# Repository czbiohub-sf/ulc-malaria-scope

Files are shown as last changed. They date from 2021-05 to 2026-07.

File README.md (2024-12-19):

# Remoscope: a label-free imaging cytometer for malaria diagnostics

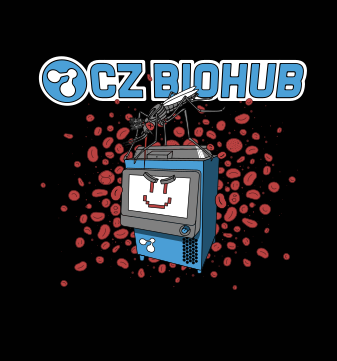
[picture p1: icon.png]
An artistic rendition of the Remoscope


## Introduction
This repository hosts instrument control software for the Remoscope, an automated and low-cost malaria diagnostic system, requiring minimal user training. The Remoscope was developed by the Bioengineering team at the Chan Zuckerberg Biohub San Francisco (CZBSF). The Remoscope images unstained fresh whole blood in liquid form and can screen up to two million red blood cells for _Plasmodium falciparum_ parasites. 

Please see our preprint here:



The Remoscope runs off a Raspberry Pi 4 Model B 8GB and an Intel Neural Compute Stick 2 (no longer available) to accelerate on-device neural network inferencing. The instrument control software is written in Python 3.7.3.

## Repository structure

```
├── ulc_mm_package
│   ├── utilities
│   ├── summary_report
│   ├── neural_nets
│   ├── image_processing
│   ├── hardware
│   ├── configs
│   ├── QtGUI
│   ├── scope_constants.py
├── OS_instructions
│   ├── OS_setup.md
│   └── OS_flash.md
├── architecture_description
├── setup.py
└── README.md
```

For a more detailed description of each folder and its scripts, see the `architecture_description/` folder.

## Installation and use

NOTE: If you are using a version downstream of commit `283a823` on `develop` (2024-03-06), you will need to install the `stats_utils` module. To do so, in the root directory run
```
python3 -m pip install -e .
```

### Option 1: Clone the image

1. Flash a pre-existing image to an SD card (must be at least 32GB), see `OS_flash.md`

### Option 2: Manual install

1. Follow the instructions under `OS_instructions`.

## Operation

To start the software, navigate to ulc_mm_package/QtGUI and run `python3 oracle.py`.

To use developer mode, navigate to ulc_mm_package/QtGUI and run `python3 dev_run.py`. This opens a GUI with manual hardware control for debugging purposes.

#### Related repositories
1. Object detection - YOGO: https://github.com/czbiohub-sf/yogo
2. Autofocus - SSAF: https://github.com/czbiohub-sf/ulc-malaria-autofocus
3. Data processing utilities / model evaluations: https://github.com/czbiohub-sf/lfm-data-utilities/
4. Statistics utilities: https://github.com/czbiohub-sf/remo-stats-utils

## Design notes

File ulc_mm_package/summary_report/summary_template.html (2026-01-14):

# Remoscope experiment report: {{ dataset_name }}

# RESEARCH USE ONLY - NOT FOR CLINICAL USE

/

Estimated parasitemia is indicated by central bar below, with 95% confidence interval outlined by box. 

{# Experiment metadata #}

Experiment metadata
Operator ID | {{ operator_id }}
Non-identifying sample ID | {{ sample_id }}
Notes | {{ notes }}
Flowcell ID | {{ flowcell_id }}

{# Estimated sample composition #}
Estimated sample composition
Class | Raw count | Parasitemia (p/uL) | Parasitemia (%)

{% for key, vals in class_name_to_cell_count.items() %}
{{key}} | {{vals[0]}} | {{vals[1]}} | {{vals[2]}}

{% endfor %} Parasitemia includes asexual stages only. {# Thumbnails #}

### Parasite thumbnails

{% for key in all_thumbnails %}
{{key.upper()}}

{% for row in all_thumbnails[key]|batch(10, "") %}

{% for filename in row %} {% if filename | length > 0 %} 
{{".".join(filename.split("_")[-1].split(".")[:2])[:4]}}
{% endif %} {% endfor %}

{% endfor %} {% endfor %} {# OPTIONAL PLOTS FOR INTERNAL USE #} {% if DEBUG_SUMMARY_REPORT %} {# Metadata plots #}

### Per-Image Metadata Plot

 {# YOGO Performance Plots #}

#### Cell counts over time



#### Confidence histograms



#### Objectness histograms

 {% endif %}

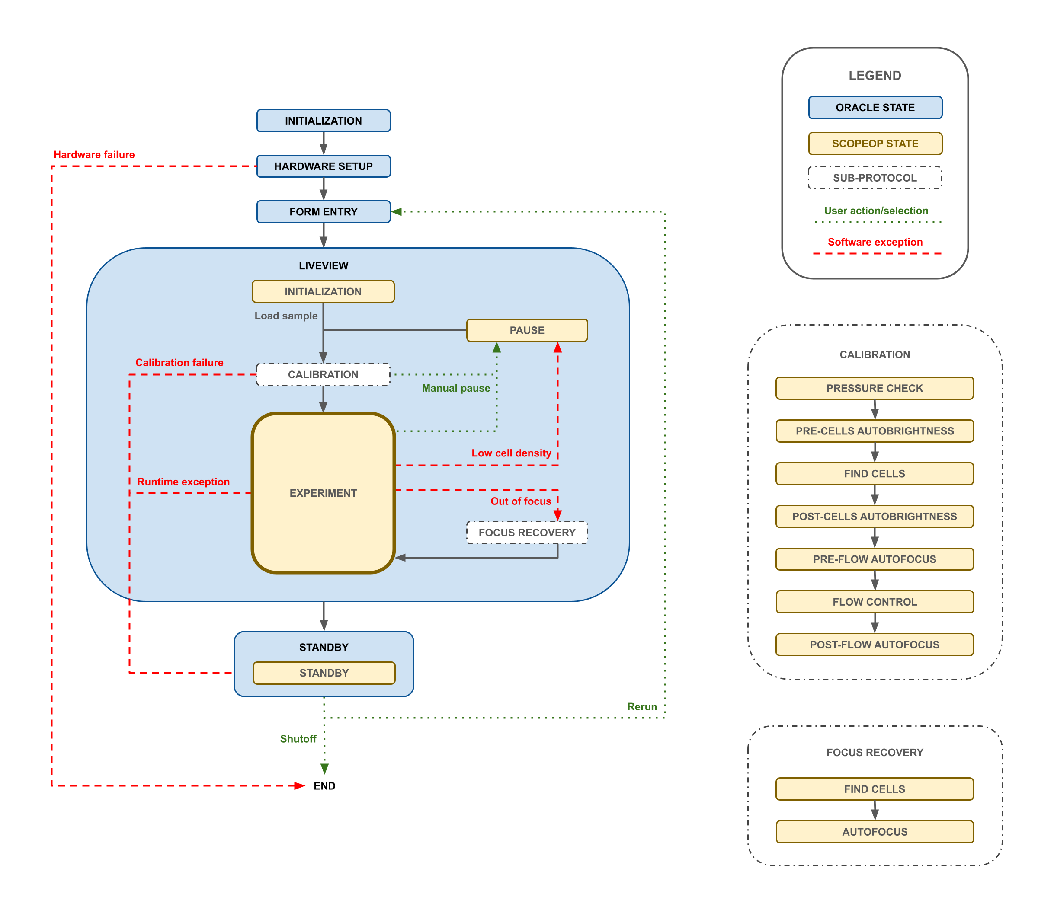
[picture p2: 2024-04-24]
software flowchart.png

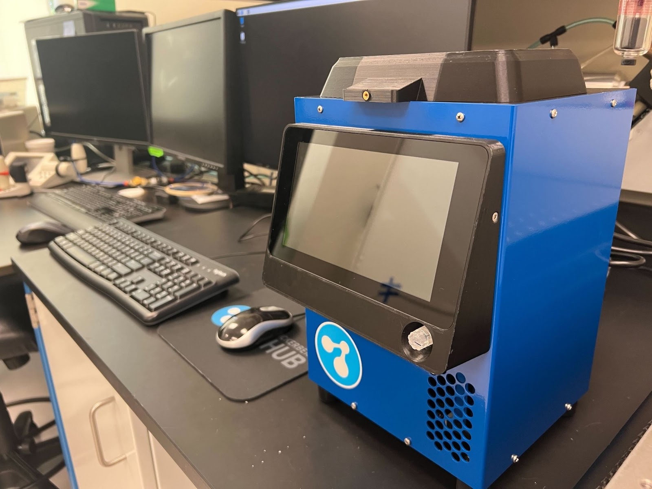
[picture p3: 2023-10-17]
pic_of_scope.jpg

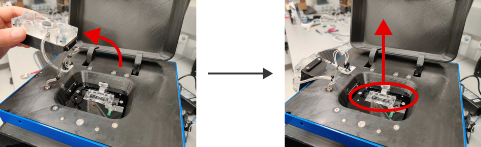
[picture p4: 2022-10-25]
ulc_mm_package/QtGUI/gui_images/remove_infographic.png

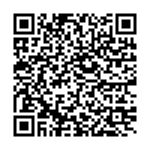
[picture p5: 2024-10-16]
ulc_mm_package/QtGUI/gui_images/QR/no-cells.png

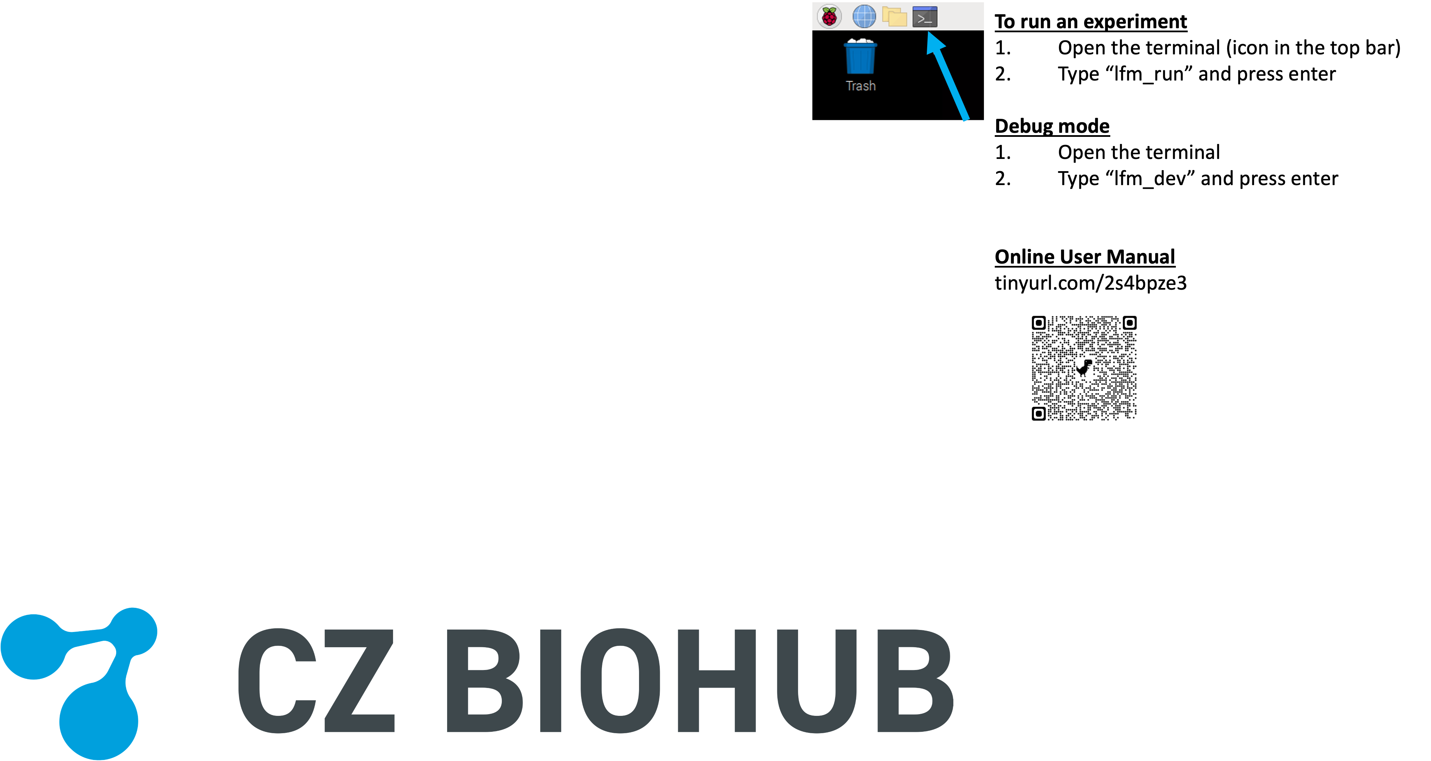
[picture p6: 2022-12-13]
ulc_mm_package/utilities/rpi_bg.png

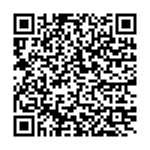
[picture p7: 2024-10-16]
ulc_mm_package/QtGUI/gui_images/QR/flowrate.png

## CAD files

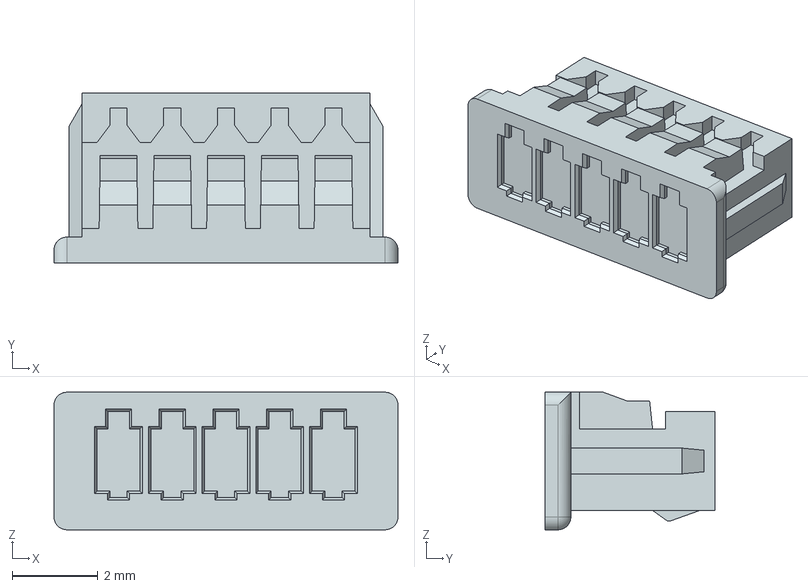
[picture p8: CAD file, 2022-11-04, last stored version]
pcb/ulc-mm/3d models/Molex_PicoBlade_533980571_Conn.step
8.00 x 3.95 x 3.20 mm

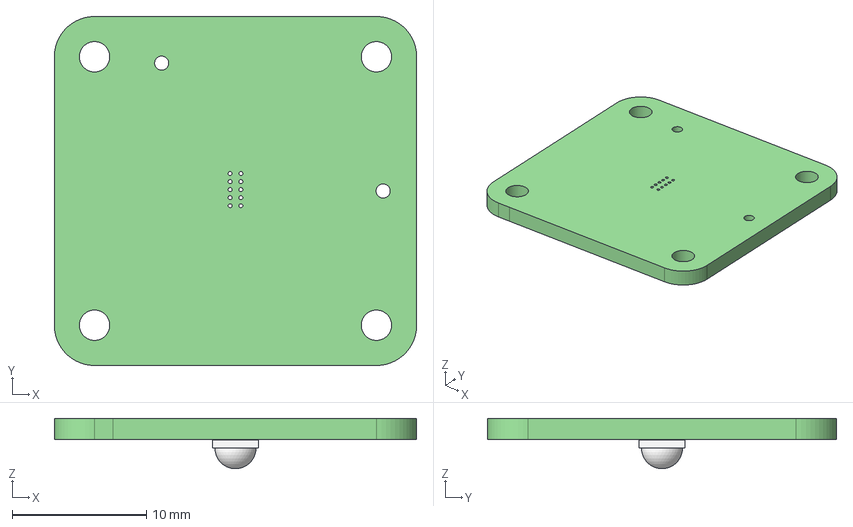
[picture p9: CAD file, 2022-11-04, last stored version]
pcb/ulc-mm/ulc-mm-led.step
27.0 x 26.0 x 3.76 mm

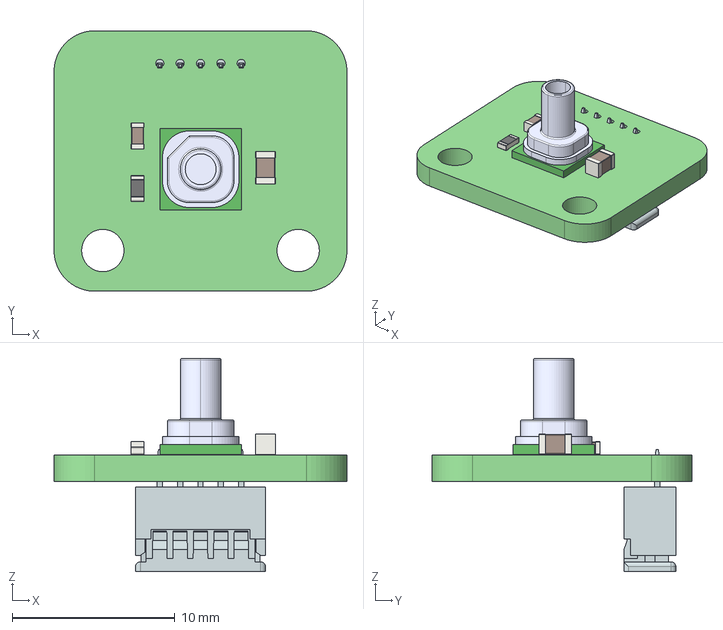
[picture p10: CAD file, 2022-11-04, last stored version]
pcb/ulc-mm/mprls.step
18.0 x 16.0 x 13.1 mm

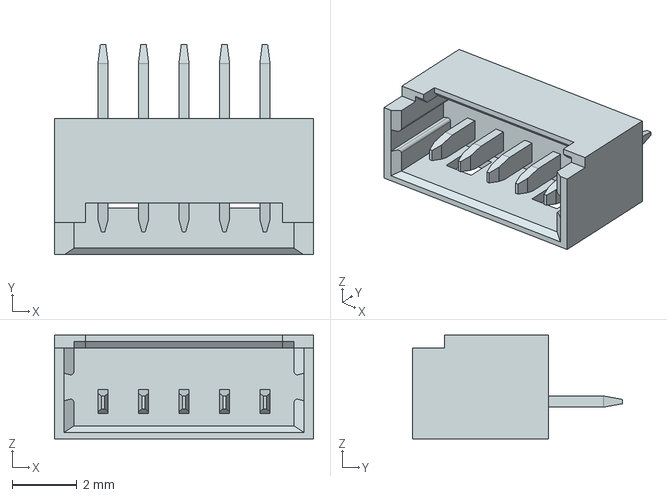
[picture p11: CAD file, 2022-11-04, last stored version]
pcb/ulc-mm/3d models/Molex_530470510.stp
8.00 x 6.50 x 3.20 mm

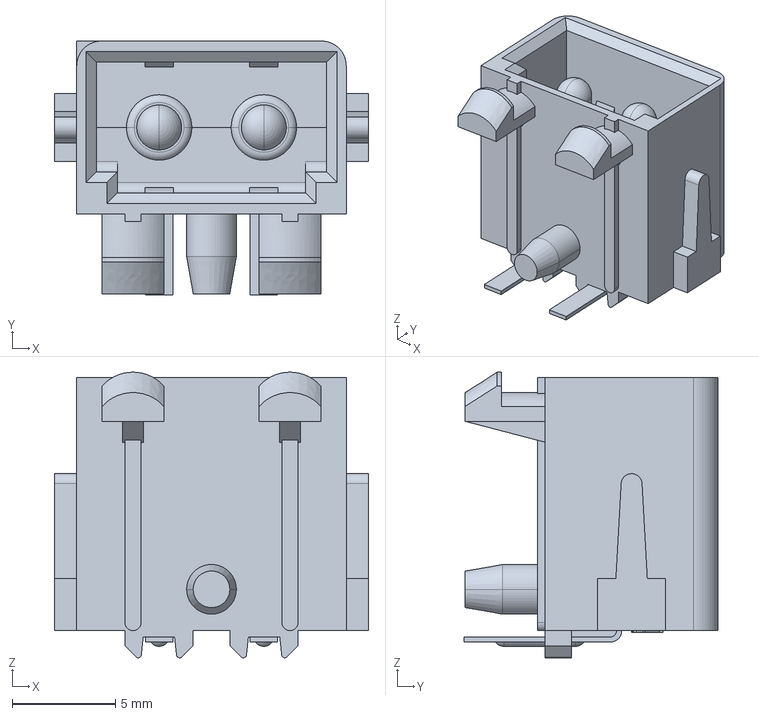
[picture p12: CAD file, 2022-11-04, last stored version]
pcb/ulc-mm/3d models/TE_794120-1-g-3d.stp
15.2 x 12.3 x 13.9 mm

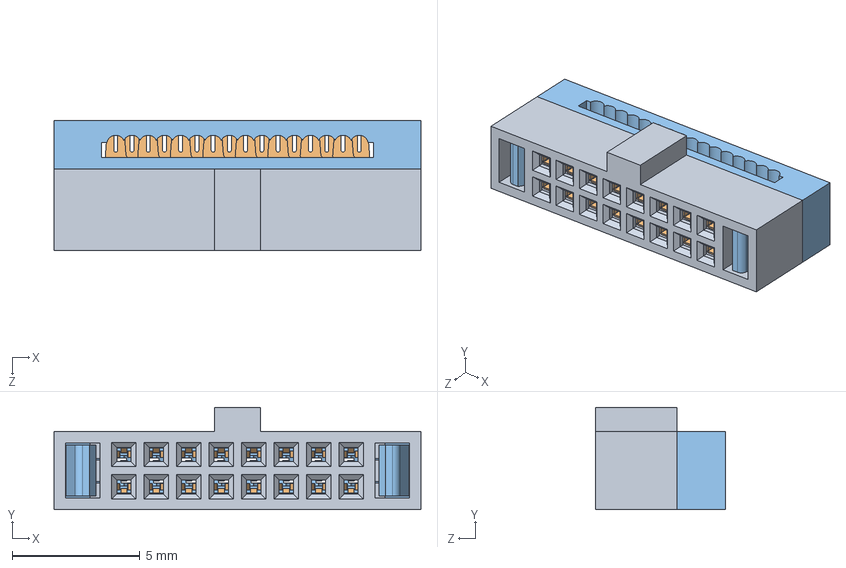
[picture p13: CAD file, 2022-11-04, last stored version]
pcb/ulc-mm/3d models/3230-16-0102-00 3D.STEP
14.4 x 4.00 x 5.10 mm
802-4412-440XX x 16
801-4412-16-ZIF

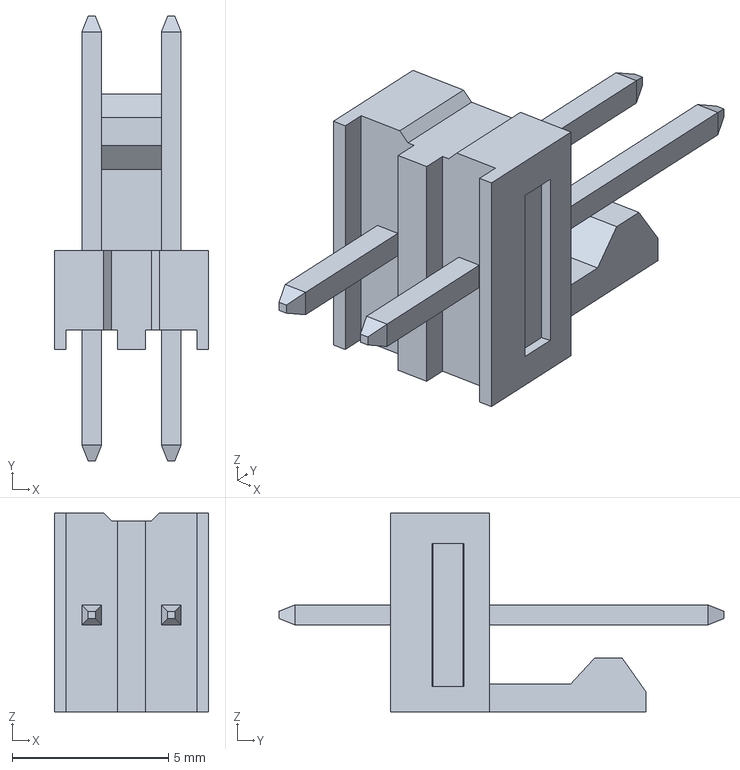
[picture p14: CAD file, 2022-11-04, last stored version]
pcb/ulc-mm/3d models/Molex_KK_022232021.stp
4.93 x 14.2 x 6.35 mm

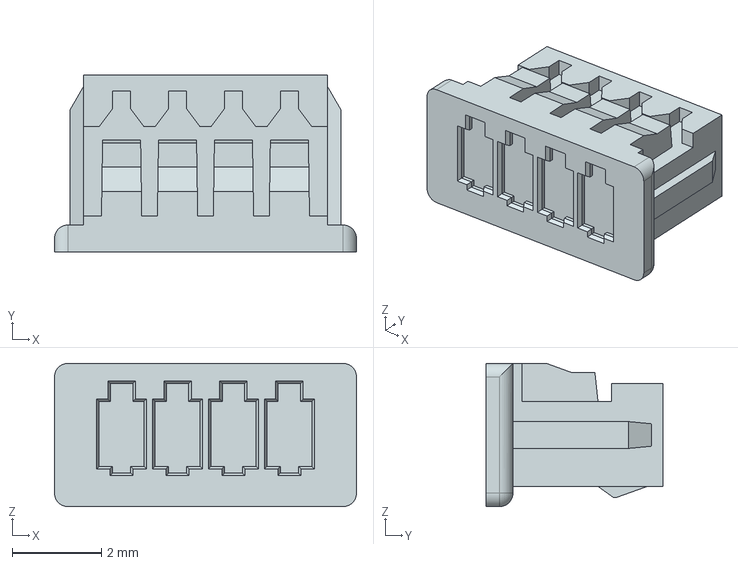
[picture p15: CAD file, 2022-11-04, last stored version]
pcb/ulc-mm/3d models/Molex_PicoBlade_530470410_Conn.step
6.75 x 3.95 x 3.20 mm

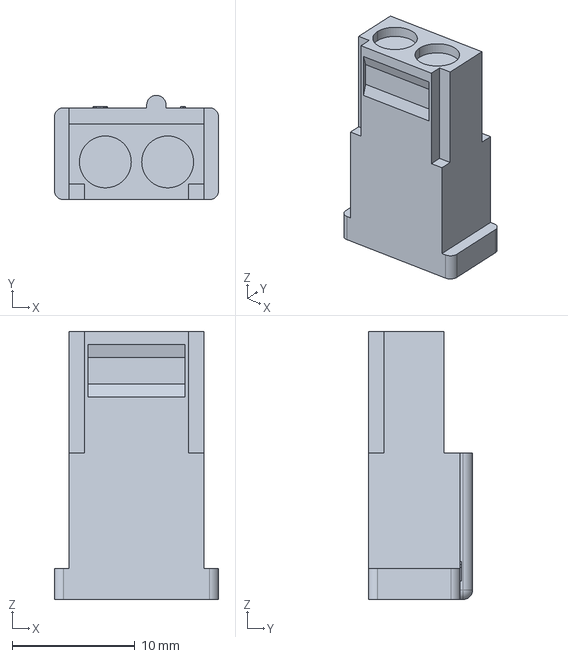
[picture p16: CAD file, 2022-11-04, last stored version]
pcb/ulc-mm/3d models/c-1-480318-0-r-3d.stp
13.4 x 8.51 x 21.8 mm

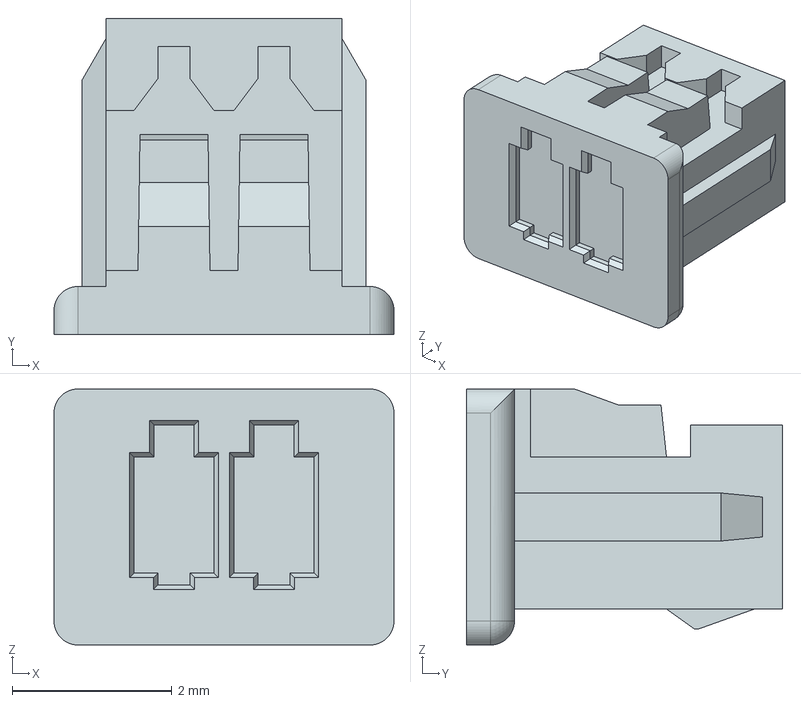
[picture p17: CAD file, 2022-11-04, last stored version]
pcb/ulc-mm/3d models/Molex_PicoBlade_530470210_Conn.step
4.25 x 3.95 x 3.20 mm

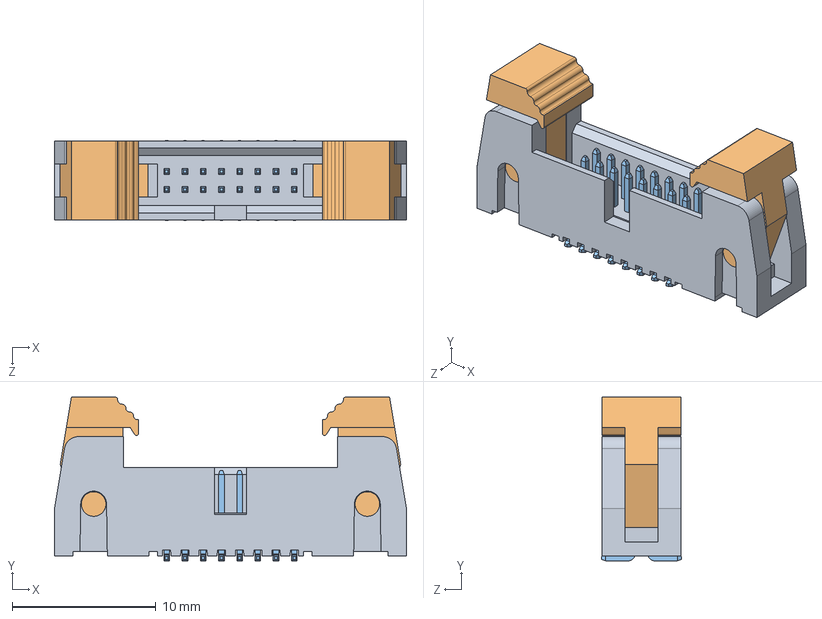
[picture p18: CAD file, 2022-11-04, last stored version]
pcb/ulc-mm/3d models/3210-16-003-12-00 3D.STEP
24.5 x 11.4 x 5.60 mm
804A-2196-01 x 2
802-2196SM x 16

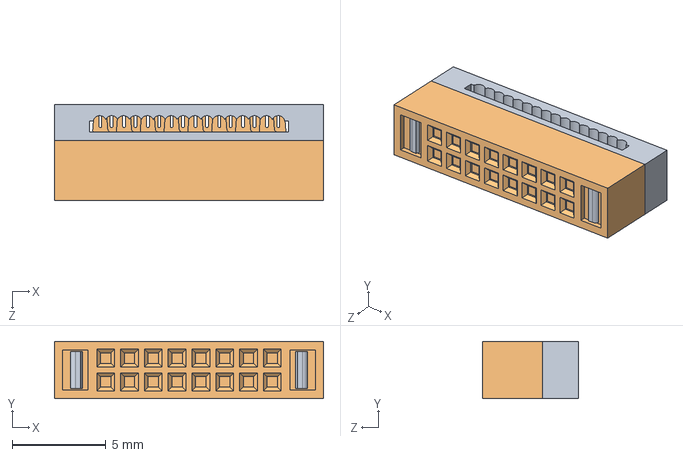
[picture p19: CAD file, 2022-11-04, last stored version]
pcb/ulc-mm/3d models/3230-16-0101-00 3D.STEP
14.4 x 3.05 x 5.10 mm

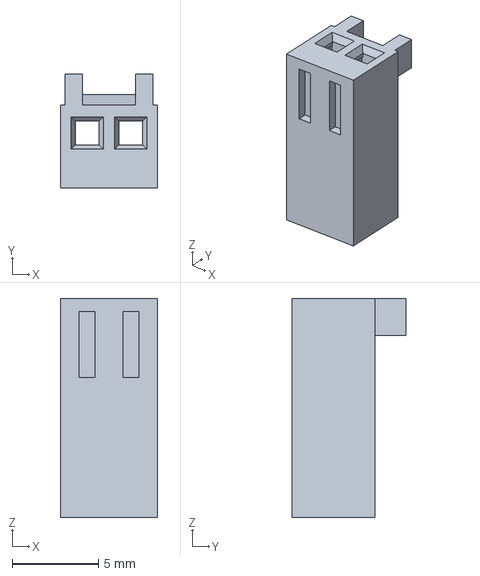
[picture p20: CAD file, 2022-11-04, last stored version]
pcb/ulc-mm/3d models/022013027.stp
5.64 x 6.63 x 12.7 mm

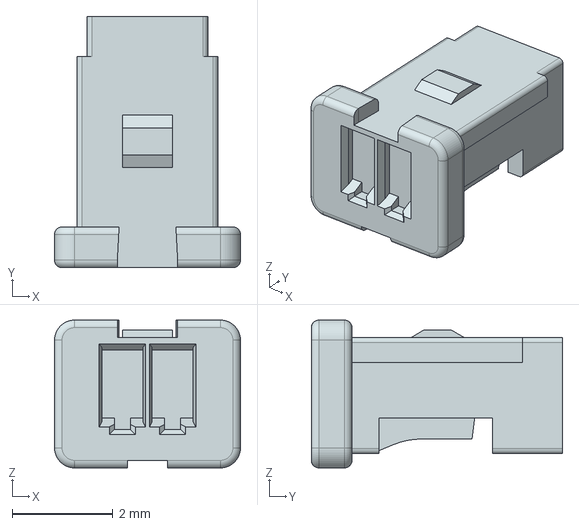
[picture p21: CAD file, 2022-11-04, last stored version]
pcb/ulc-mm/3d models/5013300200.stp
3.70 x 5.00 x 2.94 mm

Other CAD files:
pcb/ulc-mm/3d models/5013310207.stp

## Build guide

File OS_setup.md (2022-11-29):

Install Raspbian GNU/Linux 11 (bullseye) on a fresh 64GB SD card. Make sure to update the OS
hostname and wifi/password by pressing shift-ctrl-x. After it is flashed, pop it into a Pi and
follow the commands below.

### Starting out
```console
sudp apt update
sudo apt upgrade
```

### Install ulc-malaria-scope
```console
mkdir Documents && cd Documents
git clone https://github.com/czbiohub/ulc-malaria-scope.git
cd ulc-malaria-scope
pip3 install -e .
```

### Install cmake and some req'd libraries
```console
sudo apt install -y cmake
sudo apt install libusb-1.0-0-dev
sudo apt install libatlas-base-dev
```

### Install Openvino

Please note: I found that a *lot* of the documentation for the installation of Openvino is simply wrong. I suspect that it is way out of date, and nobody at Intel bother to update it. The instructions I have below are the result of what I found to work, but it could change in future Openvino versions. A *large* part of figuring it out was looking at the post-install setup scripts that openvino wrote (primarily setupvars.sh and install_NCS_udev_rules.sh), figuring out what those scripts were *supposed* to do, and doing those steps. At the very least, you learn a lot about linux when installing all of this ;)

```console
git clone https://github.com/openvinotoolkit/openvino.git
git checkout tags/2022.1.1
git submodule update --init --recursive
mkdir build && cd build

# Takes a long time! Maybe ~4 hrs?
cmake \
  -DCMAKE_BUILD_TYPE=Release \
  -DENABLE_PYTHON=ON \
  -DPYTHON_EXECUTABLE="/usr/bin/python3"  \
  -DPYTHON_LIBRARY="/usr/lib/arm-linux-gnueabihf/libpython3.9.so"  \
  -DPYTHON_INCLUDE_DIR="/usr/include/python3.9"  \
  -DCYTHON_EXECUTABLE="/home/pi/.local/bin/cython"  \
  -DENABLE_OV_TF_FRONTEND_ENABLE=OFF  \
  -DENABLE_OV_PDPD_FRONTEND_ENABLE=OFF  \
  -DENABLE_SAMPLES=OFF  \
  -DENABLE_HETERO=OFF  \
  .. && make --jobs=$(nproc --all)
```

### Add the openvino Python libraries to the `PYTHONPATH`
```console
export PYTHONPATH=/home/pi/openvino/bin/armv7l/Release/lib/python_api/python3.9:$PYTHONPATH
```

### Manually update NCS2 udev rules

```console
# add yourself to group
sudo usermod -a -G users "$(whoami)"

# Now find the file "97-myriad-usbboot.rules" - for me, it was at
#   /home/pi/openvino/src/plugins/intel_myriad/third_party/mvnc/src/97-myriad-usbboot.rules
# If yours is in a different place, replace my path with yours below

sudo cp /home/pi/openvino/src/plugins/intel_myriad/third_party/mvnc/src/97-myriad-usbboot.rules /etc/udev/rules.d/
sudo udevadm control --reload-rules
sudo udevadm trigger
sudo ldconfig
```

### Install Vimba

I could not find Vimba for `armv71` online. I `rsync`'d the source (Vimba for Linux ARMv7 32-bit - Release Notes) from a previous Malaria Scope's OS and installed
from there.

I `rsync`'d it to `/opt/`, then
```console
cd /opt/Vimba_5_0/VimbaUSBTL
sudo ./Install.sh
sudo reboot
```

after reboot,

```console
cd /opt/Vimba_5_0/VimbaPython
sudo ./Install.sh
```

### Updating boot/config.txt
Now is a good time to take a breath. You've made it through the worst of it!
Add the following to `/boot/config.txt` (at the bottom, under `[all]` if it is there)

```console
start_x=1
dtoverlay=pwm-2chan,pin=12,func=4,pin2=13,func2=4
gpu_mem=128
```

Uncomment the following

```console
dtparam=i2c_arm=on
```

and now reboot.

### Install Others

To automate running the daemon at boot time, run:

```console
sudo systemctl enable pigpiod
```

### Instantiate our ulc-malaria-scope services

```console
sudo cp ~/Documents/ulc-malaria-scope/ulc_mm_package/utilities/systemd_init_scripts/init_led_pneumatic.service /lib/systemd/system
sudo chmod 644 /lib/systemd/system/init_led_pneumatic.service

sudo cp ~/Documents/ulc-malaria-scope/ulc_mm_package/utilities/systemd_init_scripts/fan.service /lib/systemd/system
sudo chmod 644 /lib/systemd/system/fan.service

sudo cp ~/Documents/ulc-malaria-scope/ulc_mm_package/utilities/systemd_init_scripts/ngrok.service /lib/systemd/system
sudo chmod 644 /lib/systemd/system/ngrok.service

sudo systemctl daemon-reload
sudo systemctl enable init_led_pneumatic.service
sudo systemctl enable fan.service
sudo systemctl enable ngrok.service
```

### Setting up ngrok
[Ngrok](https://ngrok.com/) is a service used to create `ssh` tunnels for accessing our scopes when they are behind private networks. At the time of writing (2022-11-28),
`ngrok` free-tier accounts allow you to have one persistent `ssh` connection per account.

Each scope needs to sign up for its own ngrok account (using a unique email) to be able to open and maintain a persistent ssh connection when the program starts.
To create an `ngrok` account, "Google Distribution email accounts" (i.e a forwarding received emails-only email account)
are sufficient. (According to IT at the time of writing, having an inbound/outbox default @czbiohub.org mailbox costs $7/mo.)

1. Ask IT to make a new account for the scope (and ask them to set your email as the forwarding one), e.g `lfm_newscope@czbiohub.org`
2. Sign up for `ngrok`, and note down the unique token.
3. Add this token to the scope's persistent environment variables by doing the following:
  - Open the bashrc file: `nano /home/pi/.bashrc`
  - Add `export NGROK_AUTH_TOKEN=<TOKEN_HERE>` to the bottom of the file.
4. TODO - set up the emailing functionality (`lfm_central@czbiohub.org`) (instead of each scope having a regular mailbox, which costs $7/mo for a
@czbiohub.org address, we have a single @czbiohub.org address that all the scopes use to send emails.) **Fill this in with details once we have this implemented.

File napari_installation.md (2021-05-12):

``` 
python3 -m venv napari
source napari/bin/activate
git clone https://github.com/czbiohub/napari-bb-annotations.git
git checkout pranathi-tflite
pip3 install --upgrade pip
pip3 install -r requirements_pip4.txt
sudo apt-get update
sudo apt-get install -y qt5-default pyqt5-dev pyqt5-dev-tools
```

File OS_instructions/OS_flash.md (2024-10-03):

# Flashing Instructions

99% of the time, you will be flashing one of these images. They are pre-made and ready specifically for the ULC Malaria Scope.

First, go get the Raspberry Pi Imager, if you don't have it already:

https://www.raspberrypi.com/software/

Second, go to the drive link:

https://drive.google.com/drive/u/0/folders/1lGbjsn2M_-sXlK0GY4xKjBfApmT6D6bf

Download the most recent image (currently in folder `2022-11-28 Base OS`) - it should be a `.img` or `.img.xz` file.

Now you simply flash the image. Open the program, plug in your SD card, and follow these options:

- For "Operating System", choose the `.img` or `.img.xz` file that you downloaded. This will be under "Custom" images
- For "Storage", choose the SD card

Next, press "shift-control-x" and update some settings such as the hostname and wifi.

Now, simply click "Write" and let the program finish.

## Post Flash

The first step here will be to insert the SD card into a Raspberry Pi and access it. Either `ssh` into it (make sure you have the hostname!), or plug a keyboard and monitor into it. Then, open a terminal, and run the following commands:

```console
cd ~/Documents/ulc-malaria-scope
git pull  # enter your ghp keys here, if necessary
```

### Setting up ngrok

[Ngrok](https://ngrok.com/) is a service used to create `ssh` tunnels for accessing our scopes when they are behind private networks. At the time of writing (2022-11-28), `ngrok` free-tier accounts allow you to have one persistent `ssh` connection per account.

Each scope needs to sign up for its own ngrok account (using a unique email) to be able to open and maintain a persistent ssh connection when the program starts. To create an `ngrok` account, "Google Distribution email accounts" (i.e a forwarding received emails-only email account) are sufficient. (According to IT at the time of writing, having an inbound/outbox default @czbiohub.org mailbox costs $7/mo.)

1. Ask IT to make a new account for the scope (and ask them to set your email as the forwarding one), e.g `lfm_newscope@czbiohub.org`
2. Sign up for `ngrok`, and note down the unique token.
3. Add this token to the scope's persistent environment variables by doing the following:
  - Open the bashrc file: `nano /home/pi/.bashrc`
  - Add `export NGROK_AUTH_TOKEN=<TOKEN_HERE>` to the bottom of the file.

### Setting up email functionality for sending back the ngrok address automatically
We use a non Biohub free gmail account to do basic email sending. The email, `lfmscope@gmail.com` sends an email to itself which is then forwarded to all the people on its forwarding list.
Gmail allows you to generate a unique password for each new device that you want to run on. Instructions to generate application-specific-passwords are [here](https://support.google.com/accounts/answer/185833?hl=en). Every microscope needs to have its own unique application-specific-password.
1. Create an application specific password using the `lfmscope@gmail.com` account
2. Place the password in the microscope's persistent environment variables (similar to what we did above for `ngrok`):
  - Open the bashrc file: `nano /home/pi/.bashrc`
  - Add `export GMAIL_TOKEN=<TOKEN_HERE>` to the bottom of the file.
3. Run both `oracle.py` and `dev_run.py` to ensure you're receiving emails and that there are no errors (for example, if you forget to set the email token, that will raise a custom `EmailError: no token set` error. Similarly if an ngrok token isn't set, a custom `NgrokError: no token set` error will be raised.)

### Setting up bash aliases
1. To avoid users having to enter in an arduous path into the terminal to run a program (which is also likely to be error-prone), we have a few bash aliases instead. These aliases are stored under `ulc-malaria-scope/ulc_mm_package/utilities/.bash_aliases`. `cd` into that directory and `cp` that file to `/home/pi`, i.e:
```
cd Documents/ulc-malaria-scope/ulc_mm_package/utilities
cp .bash_aliases /home/pi
```

The commands in the file can now be run from the terminal. At the time of writing (2022-12-09), the following commands are available:
- `lfm_run` - runs `oracle.py`
- `lfm_dev` - runs `dev_run.py`
- `send_address` - runs `email_utils.py` (attempts to send the ngrok address to `lfmscope@gmail.com`)

### Setting a default location
- In `~/.bashrc` add the following environment variable at the bottom of the file: `DEFAULT_SITE='NAME_OF_SITE'`. Note: the specified site MUST already be listed in `ulc_mm_package/QtGUI/gui_constants.py`'s `SITE_LIST` constant.

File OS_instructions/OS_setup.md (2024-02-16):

# Creating a fresh OS from scratch

These are instructions for creating a fresh OS image from scratch. 99% of the time, you will most likely just want to flash one of our pre-made images - see `OS_flash.md`.

## Full Installation Instructions

Install Raspbian GNU/Linux 11 (Bullseye) on a fresh 64GB SD card. Make sure to update the OS
hostname and wifi/password by pressing shift-ctrl-x. After it is flashed, pop it into a Pi and
follow the commands below.

```console
sudo apt update
sudo apt upgrade
```

## Optional but very nice things (axel would deeply appreciate it)

```console
sudo apt install tmux
cat << EOF > ~/.vimrc
set ai
set ruler
set hlsearch
set showmatch
set incsearch
set expandtab
set lazyredraw
set noswapfile
set splitbelow
set splitright
set ignorecase
set smartcase
set wildmenu
set number relativenumber

set mouse=a
set laststatus=2

set tabstop=2
set scrolloff=2
set shiftwidth=2
set softtabstop=2
set encoding=utf-8
set backspace=indent,eol,start

set signcolumn=yes:1
set fillchars+=vert:\|

set updatetime=250
set timeoutlen=300 ttimeoutlen=0

filetype plugin indent on
map <C-J> <C-W><C-J>
map <C-K> <C-W><C-K>
map <C-L> <C-W><C-L>
map <C-H> <C-W><C-H>
highlight clear SignColumn
EOF
```

### Install numba first, separately
Note: this section may become obsolete once we transition to a 64-bit OS. For now, these are the steps to get numba working on Raspbian 32-bit.

```
sudo apt install llvm-11
export LLVM_CONFIG=llvm-config-11 pip install llvmlite==0.37.0 --no-cache
pip install numba==0.56.0
```

### Install ulc-malaria-scope
```console
mkdir Documents && cd Documents
git clone https://github.com/czbiohub/ulc-malaria-scope.git
cd ulc-malaria-scope
pip3 install -e .
```

### Install cmake and some required libraries
```console
sudo apt install -y cmake
sudo apt install libusb-1.0-0-dev
sudo apt install libatlas-base-dev
pip3 install Cython>=0.29.33
```

### Install Openvino

Please note: I found that a *lot* of the documentation for the installation of Openvino is simply wrong. I suspect that it is way out of date, and nobody at Intel bother to update it. The instructions I have below are the result of what I found to work, but it could change in future Openvino versions. A *large* part of figuring it out was looking at the post-install setup scripts that openvino wrote (primarily setupvars.sh and install_NCS_udev_rules.sh), figuring out what those scripts were *supposed* to do, and doing those steps. At the very least, you learn a lot about linux when installing all of this ;)

```console
cd ~
git clone https://github.com/openvinotoolkit/openvino.git
cd openvino
git checkout tags/2022.1.1
git submodule update --init --recursive
mkdir build && cd build

# Takes a long time! Maybe ~4 hrs?
cmake \
  -DCMAKE_BUILD_TYPE=Release \
  -DENABLE_PYTHON=ON \
  -DPYTHON_EXECUTABLE="/usr/bin/python3"  \
  -DPYTHON_LIBRARY="/usr/lib/arm-linux-gnueabihf/libpython3.9.so"  \
  -DPYTHON_INCLUDE_DIR="/usr/include/python3.9"  \
  -DCYTHON_EXECUTABLE="/home/pi/.local/bin/cython"  \
  -DENABLE_OV_TF_FRONTEND_ENABLE=OFF  \
  -DENABLE_OV_PDPD_FRONTEND_ENABLE=OFF  \
  -DENABLE_SAMPLES=OFF  \
  -DENABLE_HETERO=OFF  \
  .. && make --jobs=$(nproc --all)
```

If you are running a 64 bit OS, swap out `-DPYTHON_LIBRARY="/usr/lib/arm-linux-gnueabihf/libpython3.9.so"` with `-DPYTHON_LIBRARY="/usr/lib/aarch64-linux-gnu/libpython3.9.so"`.

### Add the openvino Python libraries to the `PYTHONPATH`

for a 32 bit OS,
```console
echo "export PYTHONPATH=/home/pi/openvino/bin/armv7l/Release/lib/python_api/python3.9:$PYTHONPATH" >> ~/.bashrc
```

and if you are running a 64 bit OS,
```console
echo "export PYTHONPATH=/home/pi/openvino/bin/aarch64/Release/lib/python_api/python3.9:$PYTHONPATH" >> ~/.bashrc
```

### Manually update NCS2 udev rules

```console
# add yourself to group
sudo usermod -a -G users "$(whoami)"

# Now find the file "97-myriad-usbboot.rules" - for me, it was at
#   /home/pi/openvino/src/plugins/intel_myriad/third_party/mvnc/src/97-myriad-usbboot.rules
# If yours is in a different place, replace my path with yours below

sudo cp /home/pi/openvino/src/plugins/intel_myriad/third_party/mvnc/src/97-myriad-usbboot.rules /etc/udev/rules.d/
sudo udevadm control --reload-rules
sudo udevadm trigger
sudo ldconfig
```

### Install Vimba

Download and uncompress Vimba for your version of the software:

- [Vimba 64 bit](https://drive.google.com/file/d/1_0ckwfBUPX-drv2zrvJkzIj39QkT-eUr/view?usp=share_link)
- [Vimba 32 bit](https://drive.google.com/file/d/16OUi32I5QPsywLyl9qaezAkova_Dz53e/view?usp=sharing)

`rsync` it to `/opt/`, then

```console
cd /opt/Vimba_5_0/VimbaUSBTL
sudo ./Install.sh
sudo reboot
```

after reboot,

```console
cd /opt/Vimba_5_0/VimbaPython
sudo ./Install.sh
```

### Updating boot/config.txt
Now is a good time to take a breath. You've made it through the worst of it!
Add the following to `/boot/config.txt` (at the bottom, under `[all]` if it is there)

```console
start_x=1
dtoverlay=pwm-2chan,pin=12,func=4,pin2=13,func2=4
gpu_mem=128
```

Uncomment the following

```console
dtparam=i2c_arm=on
```

### Install Others

To automate running the daemon at boot time, run:

```console
sudo systemctl enable pigpiod
```

### Instantiate our ulc-malaria-scope services

```console
sudo cp ~/Documents/ulc-malaria-scope/ulc_mm_package/utilities/systemd_init_scripts/init_led_pneumatic.service /lib/systemd/system
sudo chmod 644 /lib/systemd/system/init_led_pneumatic.service

sudo cp ~/Documents/ulc-malaria-scope/ulc_mm_package/utilities/systemd_init_scripts/fan.service /lib/systemd/system
sudo chmod 644 /lib/systemd/system/fan.service

sudo systemctl daemon-reload
sudo systemctl enable init_led_pneumatic.service
sudo systemctl enable fan.service
```

and now reboot.

### Setting up the SSD
Instructions on Confluence here: https://czbiohub.atlassian.net/l/cp/SW5bEMJ4

Tldr:
**If choosing to format as exFAT**
1. This process is straightforward - connect the SSD to your Mac, run DiskUtility, right-click and select format, choose exFAT.
2. Rename the drive to SamsungSSD by right-clicking on it and renaming.

**For ext4, the process is a little more involved**
**Warning - formatting as ext4 means it'll be a pain to try to read the SSD on your Mac computer. The performance gains (if any) are dubious, so this section should be ignored. Likely better to just use exFAT and skip all the headache**
I outline the procedure here for MacOS, but the high-level steps are similar for Windows (it may just involve different tools)

1. Connect the SSD and use e2fsprogs to format:

  - `brew install e2fsprogs`

  - `diskutil list` (note down the name of the 4TB SSD, e.g /dev/disk2)

  - Run `sudo $(brew --prefix e2fsprogs)/sbin/mkfs.ext4 /dev/disk2`

2. Connect the SSD to a Pi / Linux system

  - Set the name of the SSD

  - Run `lsblk` and note the location of the SSD (e.g `sda` or `sda2`)

  - Run `e2label /dev/sda SamsungSSD`

3. Set the permissions of the SSD

  - `cd /media/pi/` (or wherever the SSD is located)

  - `sudo chmod 777 SamsungSSD/`

### Congrats!

You are done.

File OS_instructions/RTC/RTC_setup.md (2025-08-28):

# RTC

The RTC ensures the Pi has accurate datetime regardless of Internet connection and power loss. To stay up to date, the RTC also needs to be updated whenever the Pi has correct time via network time protocol (NTP) syncing.

The instructions below configure the OS for the following behavior:
- If Pi is disconnected from internet at startup: Update system time from RTC
- If Pi successfully syncs to NTP via internet: Update RTC from system (NTP) time

## Setup instructions

The following files need to live in the Pi's `/etc/` directory:
- `rc.local` sets behavior on boot
- `dhcpcd.exit-hook` sets behavior on Internet connection

Ensure both files have executable permission:
```
sudo chmod +x rc.local
sudo chmod +x dhcpcd.exit-hook
```

## Tests (optional)

Reboot after adding the above files to start the RTC before testing.

### RTC in use

Verify system vs RTC time using `timedatectl` in terminal. You will see a printout like this:
```
               Local time: Mon 2025-08-25 15:42:07 PDT
           Universal time: Mon 2025-08-25 22:42:07 UTC
                 RTC time: Mon 2025-08-25 22:42:08
                Time zone: America/Los_Angeles (PDT, -0700)
System clock synchronized: yes
              NTP service: active
          RTC in local TZ: no
```

If the RTC did not successfully start, RTC time will be listed as `n/a`.

### System updated by RTC

Test the use case where there's no Internet connection:

First, turn off NTP sync, otherwise the time will automatically be corrected when `timedatectl` is run.
```
timedatectl set-ntp false
```

Then, manually write an incorrect date/time to the RTC.
```
sudo hwclock --set --date "01/01/2001 00:00:00"
```

Run `timedatectl` to verify the RTC's datetime.

Turn wifi off and reboot. The system time should now be the incorrect RTC time. Be patient as it can take up to 1 min for the system time to update after reconnection.

_NOTE: If you ever want to overwrite system time using the RTC on the spot, run `sudo hwclock -s`._

### RTC updated bt system (NTP) time

Test the use case where the Pi reconnects to Internet:

Turn on wifi when it was previously off or reboot Pi. Both the system time and RTC time should be correct and can be verified by running `timedatectl`

_NOTE: If you ever want to overwrite the RTC using the NTP time on the spot, run `sudo hwclock -w`._

## Supplementary info
- [hwclock](https://linux.die.net/man/8/hwclock) tool
- [timedatectl](https://www.freedesktop.org/software/systemd/man/latest/timedatectl.html) tool

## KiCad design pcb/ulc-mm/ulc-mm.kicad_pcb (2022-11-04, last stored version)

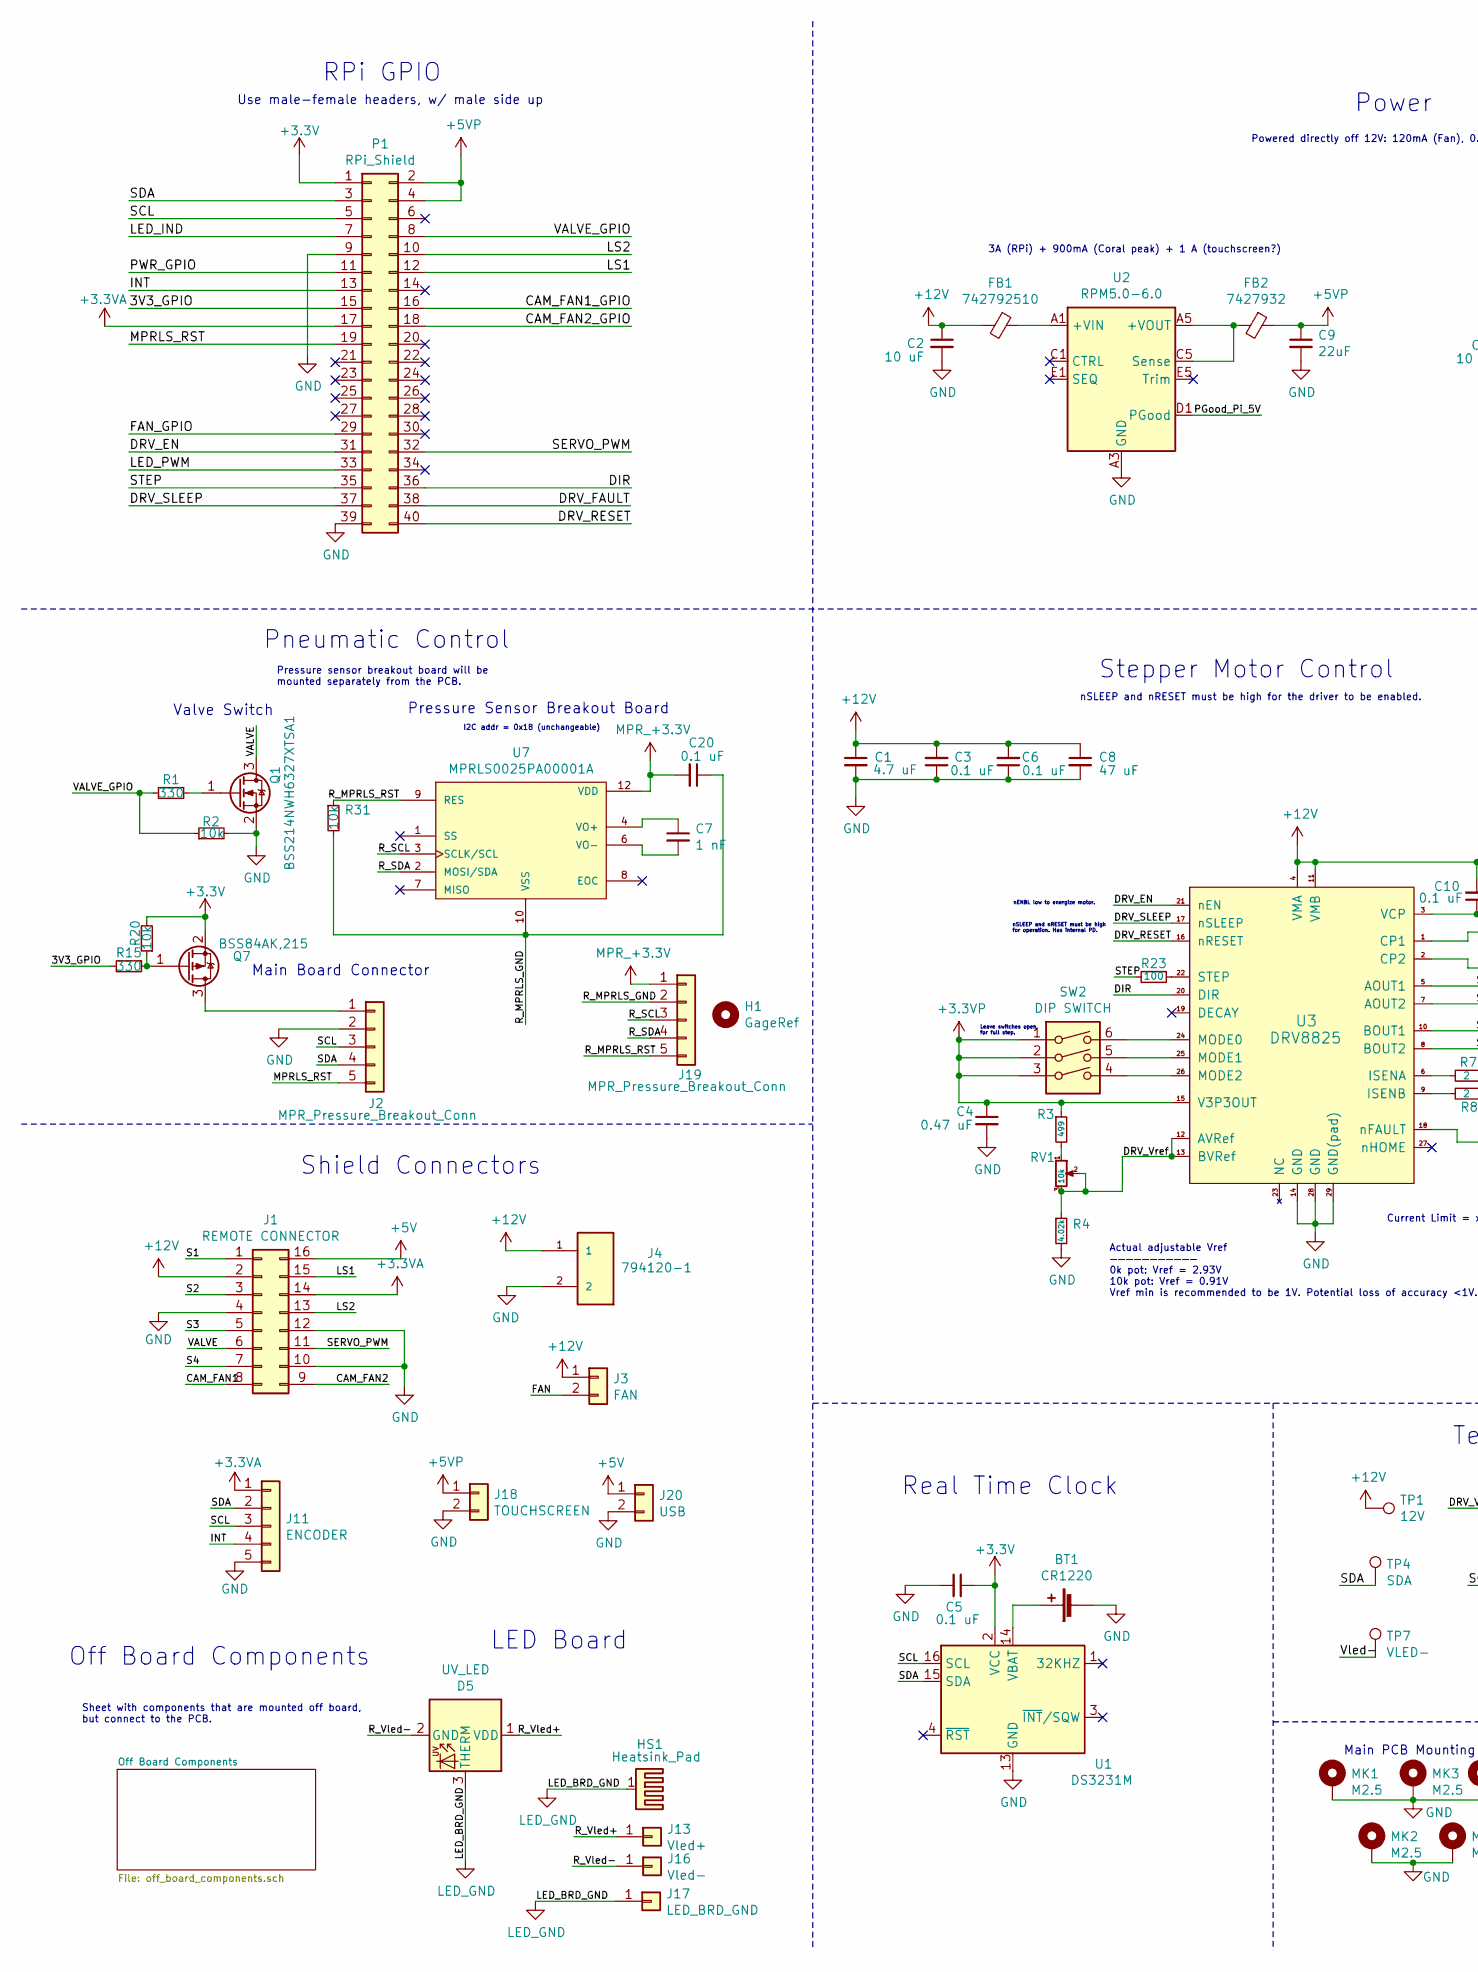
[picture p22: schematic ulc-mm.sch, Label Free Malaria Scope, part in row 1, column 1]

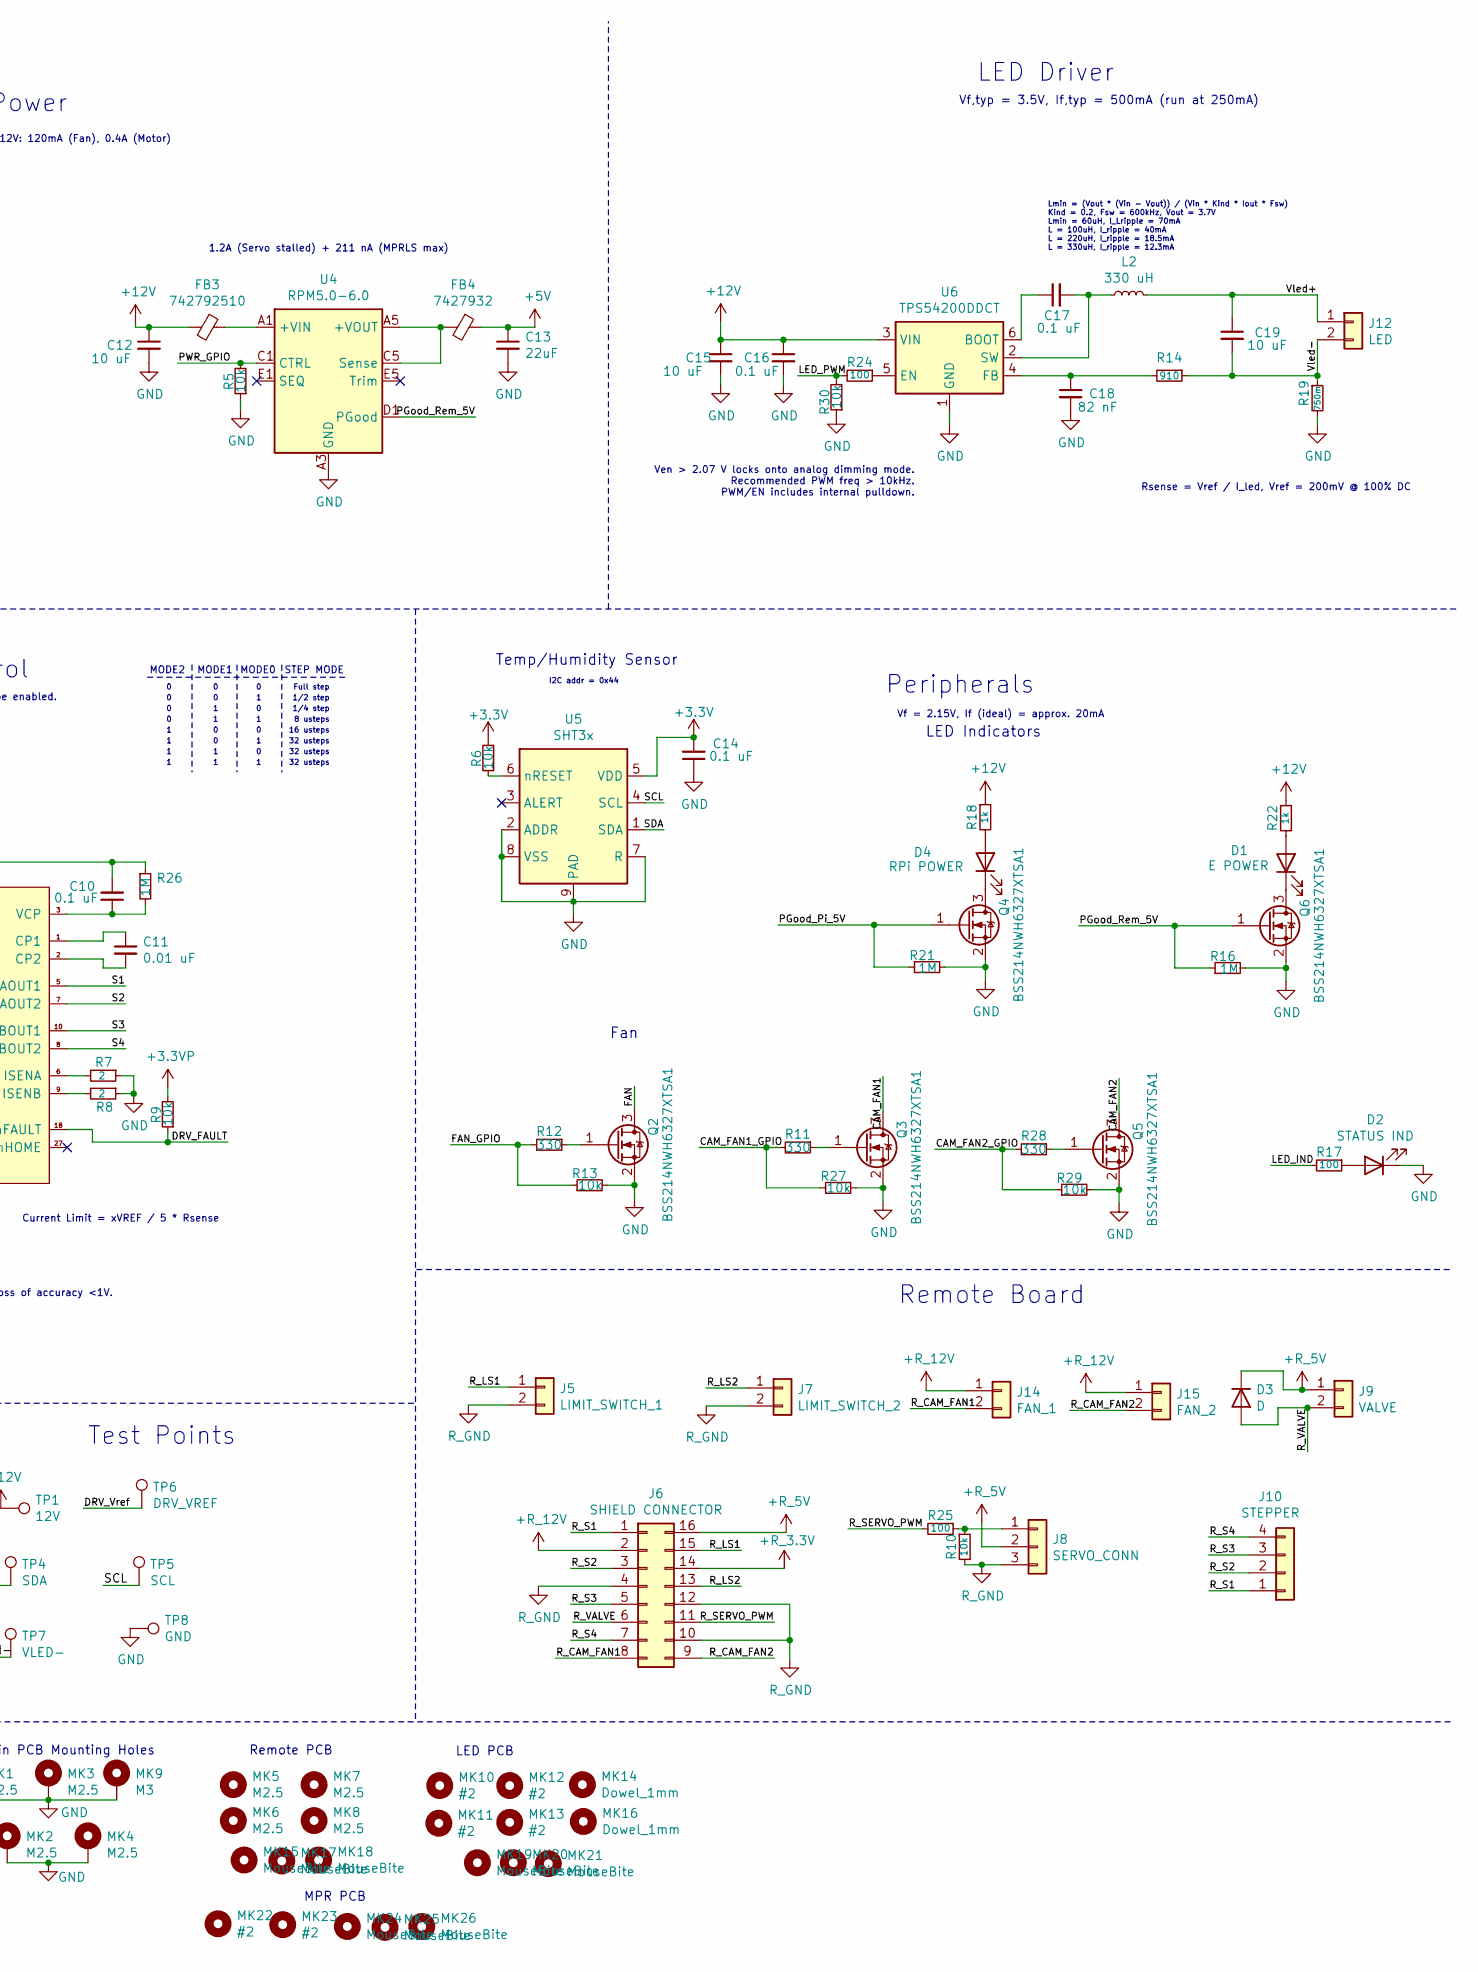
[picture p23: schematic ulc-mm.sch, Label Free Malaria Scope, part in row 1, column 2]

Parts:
BT1: CR1220; Battery_Panasonic_CR1220-VCN_Vertical_CircularHoles
C1: 4.7 uF; C_0603_1608Metric
C2, C12, C15, C19: 10 uF; C_1206_3216Metric
C3, C5, C6, C10, C14, C16, C17, C20: 0.1 uF; C_0603_1608Metric
C4: 0.47 uF; C_0603_1608Metric
C7: 1 nF; C_0805_2012Metric
C8: 47 uF; CP_Radial_D5.0mm_P2.00mm
C9, C13: 22uF; C_0805_2012Metric
C11: 0.01 uF; C_0603_1608Metric
C18: 82 nF; C_0603_1608Metric
D1: E POWER; LED_1206_3216Metric
D2: STATUS IND; LED_1206_3216Metric
D3: D; D_SMB
D4: RPi POWER; LED_1206_3216Metric
D5: UV_LED; LED_Cree-XHP35
FB1, FB3: 742792510; L_1812_4532Metric
FB2, FB4: 7427932; L_WE-PBF_7.8x4.75mm
H1: GageRef; GageRef_Hole
HS1: Heatsink_Pad; 15MMX15MM_Heatsink
J1: REMOTE CONNECTOR; PinHeader_2x08_P1.27mm_Vertical_SMD
J2, J19: MPR_Pressure_Breakout_Conn; Molex_PicoBlade_53047-0510_1x05_P1.25mm_Vertical
J3: FAN; Molex_PicoBlade_53047-0210_1x02_P1.25mm_Vertical
J4: 794120-1; TE_794120-1; PART_REV C
J5: LIMIT_SWITCH_1; Molex_PicoBlade_53047-0210_1x02_P1.25mm_Vertical
J6: SHIELD CONNECTOR; PinHeader_2x08_P1.27mm_Vertical_SMD
J7: LIMIT_SWITCH_2; Molex_PicoBlade_53047-0210_1x02_P1.25mm_Vertical
J8: SERVO_CONN; PinHeader_1x03_P2.54mm_Vertical
J9: VALVE; Molex_PicoBlade_53047-0210_1x02_P1.25mm_Vertical
J10: STEPPER; Molex_PicoBlade_53398-0471_1x04-1MP_P1.25mm_Vertical
J11: ENCODER; Molex_PicoBlade_53398-0571_1x05-1MP_P1.25mm_Vertical
J12: LED; Molex_PicoBlade_53047-0210_1x02_P1.25mm_Vertical
J13: Vled+; WirePad
J14: FAN_1; Molex_PicoBlade_53047-0210_1x02_P1.25mm_Vertical
J15: FAN_2; Molex_PicoBlade_53047-0210_1x02_P1.25mm_Vertical
J16: Vled-; WirePad
J17: LED_BRD_GND; WirePad
J18: TOUCHSCREEN; Molex_Pico-Clasp_501331-0207_1x02-1MP_P1.00mm_Vertical
J20: USB; Molex_Pico-Clasp_501331-0207_1x02-1MP_P1.00mm_Vertical
L2: 330 uH; L_Wuerth_WE-PDF_Handsoldering
MK1, MK2, MK3, MK4: M2.5; MountingHole_2.7mm_M2.5_Pad
MK5, MK6, MK7, MK8: M2.5; MountingHole_2.7mm_M2.5
MK9: M3; MountingHole_3.2mm_M3_Pad
MK10, MK11, MK12, MK13, MK22, MK23: #2; MountingHole_#2_CloseFit
MK14, MK16: Dowel_1mm; DowelPin_1mm
MK15, MK17, MK18, MK19, MK20, MK21, MK24, MK25, MK26: MouseBite; MouseBite_0.508mm
P1: RPi_Shield; PinSocket_2x20_P2.54mm_Vertical
Q1, Q2, Q3, Q4, Q5, Q6: BSS214NWH6327XTSA1; SOT-323_SC-70
Q7: BSS84AK,215; SOT-23
R1, R11, R12, R15, R28: 330; R_0805_2012Metric
R2, R5, R6, R9, R10, R13, R20, R27, R29, R30, R31: 10k; R_0603_1608Metric
R3: 499; R_0603_1608Metric
R4: 4.02k; R_0603_1608Metric
R7, R8: 2; R_0603_1608Metric
R14: 910; R_0805_2012Metric
R16, R21, R26: 1M; R_0603_1608Metric
R17, R23, R24, R25: 100; R_0603_1608Metric
R18, R22: 1k; R_0603_1608Metric
R19: 750m; R_0603_1608Metric
RV1: 10k; Potentiometer_Bourns_3266W_Vertical
SW2: DIP SWITCH; SW_DIP_SPSTx03_Slide_6.7x9.18mm_W8.61mm_P2.54mm_LowProfile
TP1: 12V; TestPoint_Keystone_5005-5009_Compact
TP4: SDA; TestPoint_Keystone_5005-5009_Compact
TP5: SCL; TestPoint_Keystone_5005-5009_Compact
TP6: DRV_VREF; TestPoint_Keystone_5005-5009_Compact
TP7: VLED-; TestPoint_Keystone_5005-5009_Compact
TP8: GND; TestPoint_Keystone_5005-5009_Compact
U1: DS3231M; SOIC-16W_7.5x10.3mm_P1.27mm
U2, U4: RPM5.0-6.0; Converter_DCDC_RECOM_RPMx.x-x.0
U3: DRV8825; TSSOP-28-1EP_W4.40mm
U5: SHT3x; DFN-8-1EP_2x2mm_P0.5mm_EP1.05x1.75mm
U6: TPS54200DDCT; SOT-23-6
U7: MPRLS0025PA00001A; XDCR_MPRLS0025PA00001A; PARTREV 03/18

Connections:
+3.3VA: J1.14, J11.1, P1.17
+3.3VP: C4.1, R3.1, R9.2, SW2.1, SW2.2, SW2.3, U3.15 (V3P3OUT)
+3V3: C5.1, C14.2, P1.1, Q7.2 (S), R6.2, R20.2, U1.2 (VCC), U5.5 (VDD)
+5V: C13.1, FB4.1, J1.16, J20.1
+5VP: C9.1, FB2.1, J18.1, P1.2, P1.4
+12V: C1.1, C2.1, C3.2, C6.2, C8.1, C10.2, C12.1, C15.1, C16.1, FB1.2, FB3.2, J1.2, J3.1, J4.1, R18.1, R22.1, R26.1, TP1.1, U3.4 (VMA), U3.11 (VMB), U6.3 (VIN)
+MPR_3.3V: C20.2, J19.1, U7.12 (VDD)
+R_3V3: J6.14
+R_5V: D3.1 (K), J6.16, J8.2, J9.1
+R_12V: J6.2, J14.1, J15.1
/3V3_GPIO: P1.15, R15.2
/CAM_FAN1: J1.8, Q3.3 (D)
/CAM_FAN1_GPIO: P1.16, R11.2, R27.1
/CAM_FAN2: J1.9, Q5.3 (D)
/CAM_FAN2_GPIO: P1.18, R28.2, R29.1
/DIR: P1.36, U3.20 (DIR)
/DRV_EN: P1.31, U3.21 (nEN)
/DRV_FAULT: P1.38, R9.1, U3.18 (nFAULT)
/DRV_RESET: P1.40, U3.16 (nRESET)
/DRV_SLEEP: P1.37, U3.17 (nSLEEP)
/DRV_Vref: R4.1, RV1.2, RV1.3, TP6.1, U3.12 (AVRef), U3.13 (BVRef)
/FAN: J3.2, Q2.3 (D)
/FAN_GPIO: P1.29, R12.2, R13.1
/INT: J11.4, P1.13
/LED_IND: P1.7, R17.2
/LED_PWM: P1.33, R24.2, R30.2
/LS1: J1.15, P1.12
/LS2: J1.13, P1.10
/MPRLS_RST: J2.5, P1.19
/PGood_Pi_5V: Q4.1 (G), R21.1, U2.D1 (PGood)
/PGood_Rem_5V: Q6.1 (G), R16.1, U4.D1 (PGood)
/PWR_GPIO: P1.11, R5.2, U4.C1 (CTRL)
/R_CAM_FAN1: J6.8, J14.2
/R_CAM_FAN2: J6.9, J15.2
/R_LS1: J5.1, J6.15
/R_LS2: J6.13, J7.1
/R_MPRLS_GND: C20.1, J19.2, R31.2, U7.10 (VSS)
/R_MPRLS_RST: J19.5, R31.1, U7.9 (RES)
/R_S1: J6.1, J10.1
/R_S2: J6.3, J10.2
/R_S3: J6.5, J10.3
/R_S4: J6.7, J10.4
/R_SCL: J19.3, U7.3 (SCLK/SCL)
/R_SDA: J19.4, U7.2 (MOSI/SDA)
/R_SERVO_PWM: J6.11, R25.2
/R_VALVE: D3.2 (A), J6.6, J9.2
/R_Vled+: D5.1 (VDD), J13.1
/R_Vled-: D5.2 (GND), J16.1
/S1: J1.1, U3.5 (AOUT1)
/S2: J1.3, U3.7 (AOUT2)
/S3: J1.5, U3.10 (BOUT1)
/S4: J1.7, U3.8 (BOUT2)
/SCL: J2.3, J11.3, P1.5, TP5.1, U1.16 (SCL), U5.4 (SCL)
/SDA: J2.4, J11.2, P1.3, TP4.1, U1.15 (SDA), U5.1 (SDA)
/SERVO_PWM: J1.11, P1.32
/STEP: P1.35, R23.2
/VALVE: J1.6, Q1.3 (D)
/VALVE_GPIO: P1.8, R1.2, R2.1
/Vled+: C19.1, J12.1, L2.2
/Vled-: C19.2, J12.2, R14.1, R19.1, TP7.1
GND: BT1.2 (-), C1.2, C2.2, C3.1, C4.2, C5.2, C6.1, C8.2, C9.2, C12.2, C13.2, C14.1, C15.2, C16.2, C18.2, D2.1 (K), J1.4, J1.10, J1.12, J2.2, J4.2, J11.5, J18.2, J20.2, MK1.1, MK2.1, MK3.1, MK4.1, MK9.1, P1.9, P1.39, Q1.2 (S), Q2.2 (S), Q3.2 (S), Q4.2 (S), Q5.2 (S), Q6.2 (S), R2.2, R4.2, R5.1, R7.1, R8.1, R13.2, R16.2, R19.2, R21.2, R27.2, R29.2, R30.1, TP8.1, U1.5 (GND), U1.6 (GND), U1.7 (GND), U1.8 (GND), U1.9 (GND), U1.10 (GND), U1.11 (GND), U1.12 (GND), U1.13 (GND), U2.A3 (GND), U2.A4 (GND), U2.B1 (GND), U2.B2 (GND), U2.B3 (GND), U2.B4 (GND), U2.C2 (GND), U2.C3 (GND), U2.C4 (GND), U2.D2 (GND), U2.D3 (GND), U2.D4 (GND), U2.D5 (GND), U2.E3 (GND), U2.E4 (GND), U3.14 (GND), U3.28 (GND), U3.29 (GND(pad)), U4.A3 (GND), U4.A4 (GND), U4.B1 (GND), U4.B2 (GND), U4.B3 (GND), U4.B4 (GND), U4.C2 (GND), U4.C3 (GND), U4.C4 (GND), U4.D2 (GND), U4.D3 (GND), U4.D4 (GND), U4.D5 (GND), U4.E3 (GND), U4.E4 (GND), U5.2 (ADDR), U5.7 (R), U5.8 (VSS), U5.9 (PAD), U6.1 (GND)
LED_GND: D5.3 (THERM), HS1.1, J17.1
unnamed: BT1.1 (+), U1.14 (VBAT)
unnamed: C7.1, U7.4 (VO+)
unnamed: C7.2, U7.6 (VO-)
unnamed: C10.1, R26.2, U3.3 (VCP)
unnamed: C11.1, U3.1 (CP1)
unnamed: C11.2, U3.2 (CP2)
unnamed: C17.1, U6.6 (BOOT)
unnamed: C17.2, L2.1, U6.2 (SW)
unnamed: C18.1, R14.2, U6.4 (FB)
unnamed: D1.1 (K), Q6.3 (D)
unnamed: D1.2 (A), R22.2
unnamed: D2.2 (A), R17.1
unnamed: D4.1 (K), Q4.3 (D)
unnamed: D4.2 (A), R18.2
unnamed: FB1.1, U2.A1 (+VIN), U2.A2 (+VIN)
unnamed: FB2.2, U2.A5 (+VOUT), U2.B5 (+VOUT), U2.C5 (Sense)
unnamed: FB3.1, U4.A1 (+VIN), U4.A2 (+VIN)
unnamed: FB4.2, U4.A5 (+VOUT), U4.B5 (+VOUT), U4.C5 (Sense)
unnamed: J2.1, Q7.3 (D)
unnamed: J8.1, R10.1, R25.1
unnamed: Q1.1 (G), R1.1
unnamed: Q2.1 (G), R12.1
unnamed: Q3.1 (G), R11.1
unnamed: Q5.1 (G), R28.1
unnamed: Q7.1 (G), R15.1, R20.1
unnamed: R3.2, RV1.1
unnamed: R6.1, U5.6 (nRESET)
unnamed: R7.2, U3.6 (ISENA)
unnamed: R8.2, U3.9 (ISENB)
unnamed: R23.1, U3.22 (STEP)
unnamed: R24.1, U6.5 (EN)
unnamed: SW2.4, U3.26 (MODE2)
unnamed: SW2.5, U3.25 (MODE1)
unnamed: SW2.6, U3.24 (MODE0)
R_GND: J5.2, J6.4, J6.10, J6.12, J7.2, J8.3, R10.2

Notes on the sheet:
Main PCB Mounting Holes
Power
Pneumatic Control
LED Driver
Peripherals
RPi GPIO
Pressure sensor breakout board will be mounted separately from the PCB.
I2C addr = 0x18 (unchangeable)
Pressure Sensor Breakout Board
Temp/Humidity Sensor
Fan
Powered directly off 12V: 120mA (Fan), 0.4A (Motor)
Use male-female headers, w/ male side up
Test Points
Stepper Motor Control
Vf,typ = 3.5V, If,typ = 500mA (run at 250mA)
I2C addr = 0x44
Shield Connectors
Remote Board
Current Limit = xVREF / 5 * Rsense
nSLEEP and nRESET must be high for operation. Has internal PD.
3A (RPi) + 900mA (Coral peak) + 1 A (touchscreen?)
1.2A (Servo stalled) + 211 nA (MPRLS max)
Real Time Clock
Lmin = (Vout * (Vin - Vout)) / (Vin * Kind * Iout * Fsw) Kind = 0.2, Fsw = 600kHz, Vout = 3.7V Lmin = 60uH, I_Lripple = 70mA L = 100uH, I_ripple = 40mA L = 220uH, I_ripple = 18.5mA L = 330uH, I_ripple = 12.3mA
Ven > 2.07 V locks onto analog dimming mode. Recommended PWM freq > 10kHz. PWM/EN includes internal pulldown.
Rsense = Vref / I_led, Vref = 200mV @ 100% DC
MODE2
MODE1
MODE0
STEP MODE
Full step
1/2 step
1/4 step
8 usteps
16 usteps
32 usteps
Actual adjustable Vref ——————————— 0k pot: Vref = 2.93V 10k pot: Vref = 0.91V Vref min is recommended to be 1V. Potential loss of accuracy <1V.
Leave switches open for full step.
Off Board Components

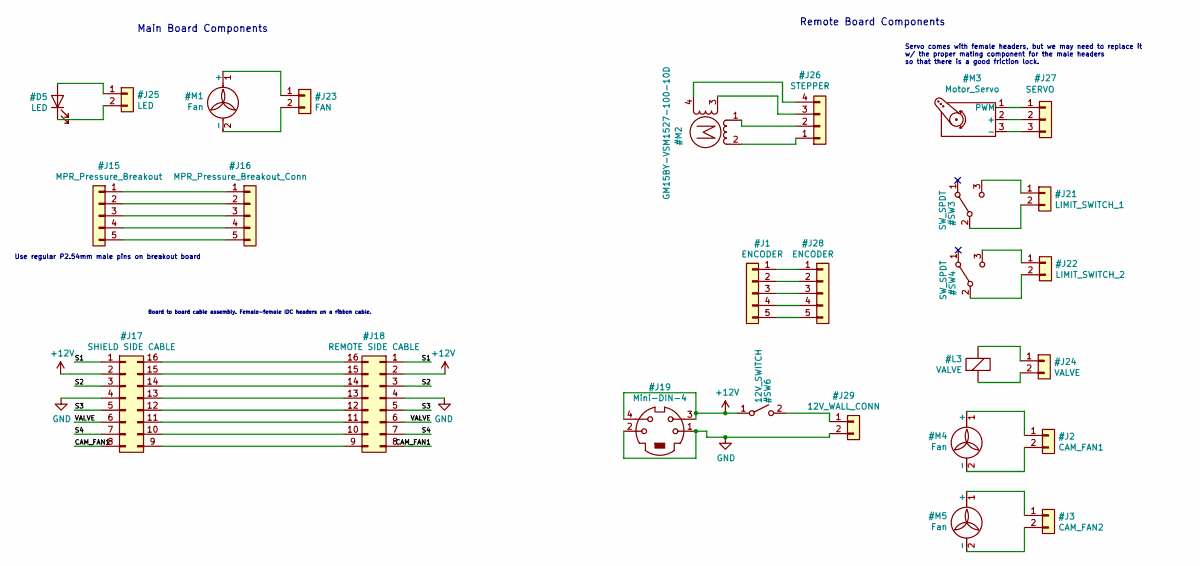
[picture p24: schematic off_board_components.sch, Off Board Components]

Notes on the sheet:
Servo comes with female headers, but we may need to replace it w/ the proper mating component for the male headers so that there is a good friction lock.
Board to board cable assembly. Female-female IDC headers on a ribbon cable.
Use regular P2.54mm male pins on breakout board
Remote Board Components
Main Board Components

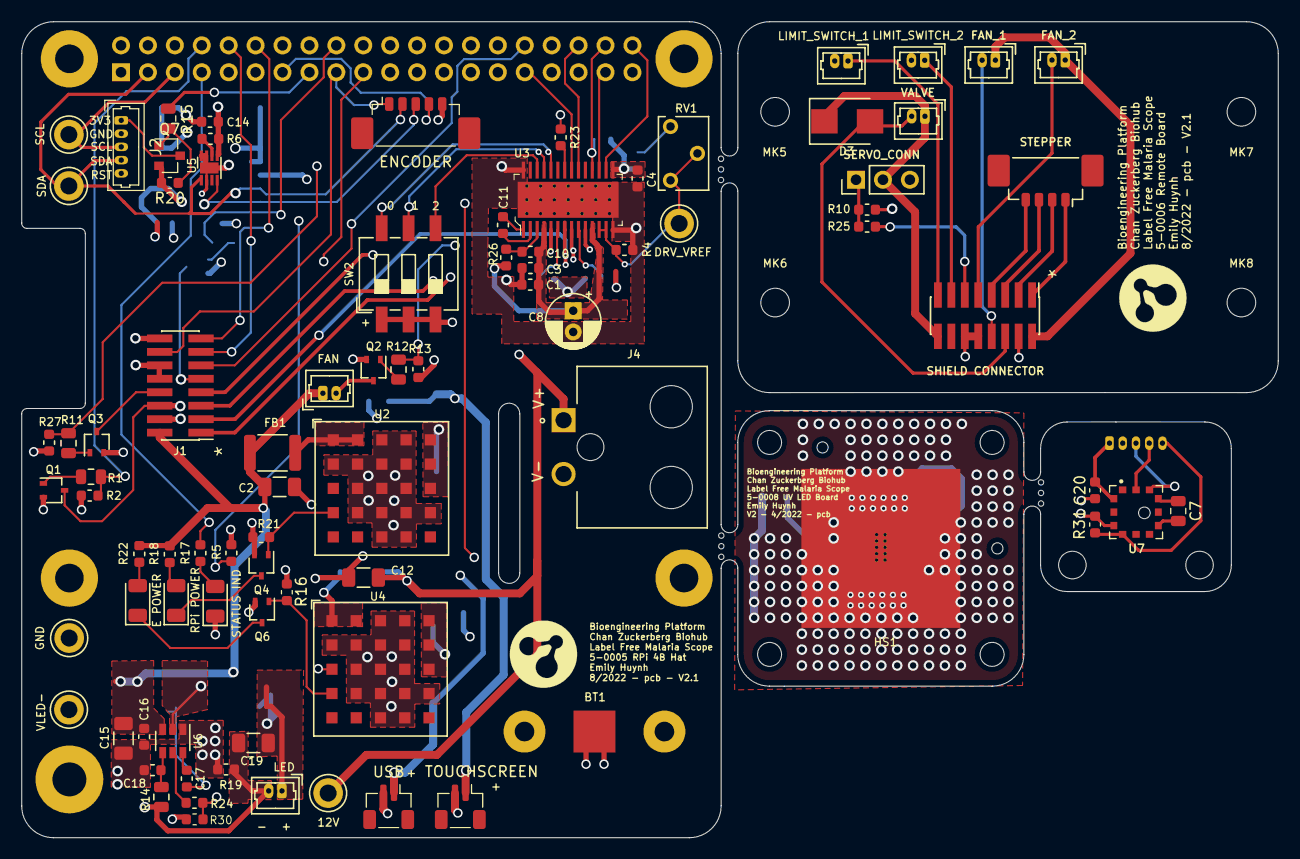
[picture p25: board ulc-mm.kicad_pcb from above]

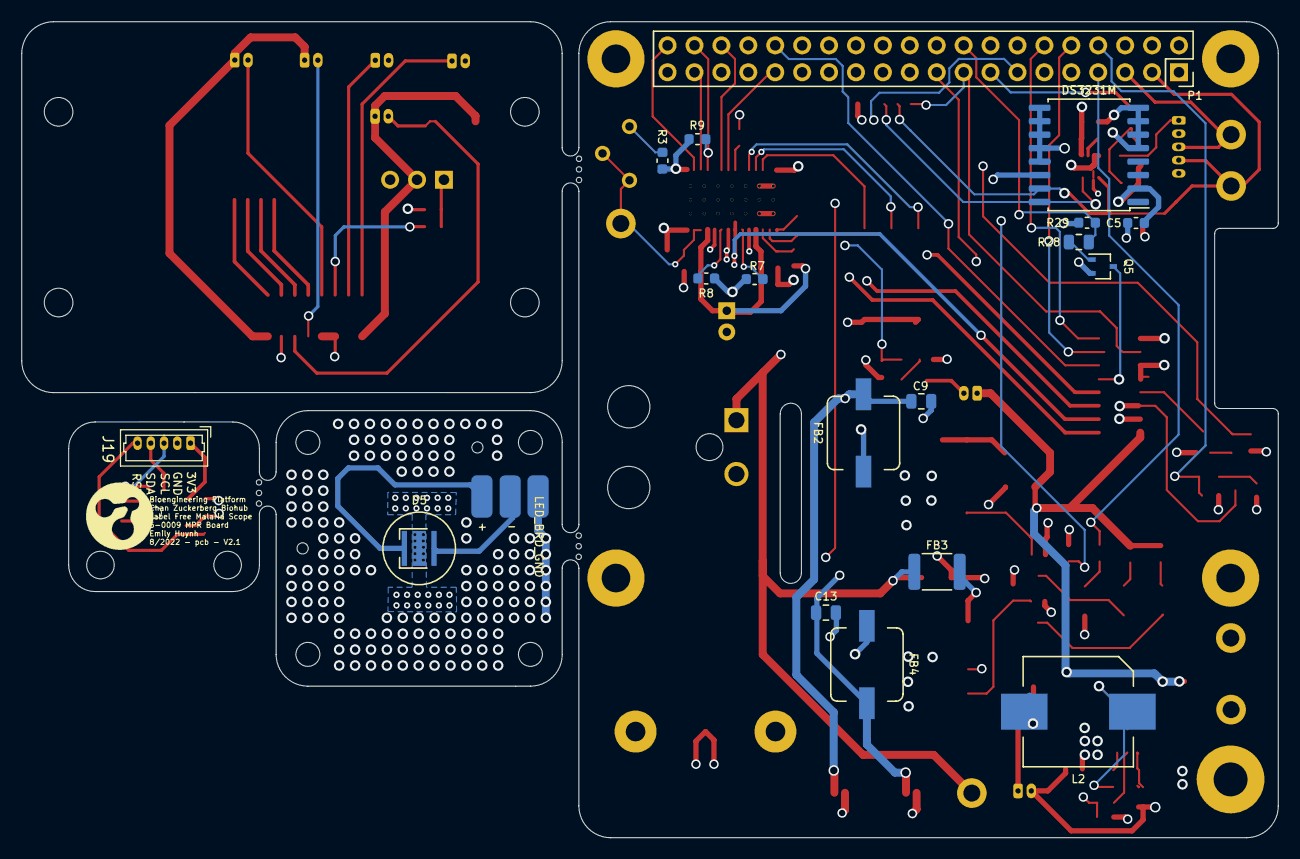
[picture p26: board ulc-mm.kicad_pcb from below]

Board: 4 copper layers, 118.6 x 77.0 mm, 132 parts (21 on the bottom side), 96 nets.

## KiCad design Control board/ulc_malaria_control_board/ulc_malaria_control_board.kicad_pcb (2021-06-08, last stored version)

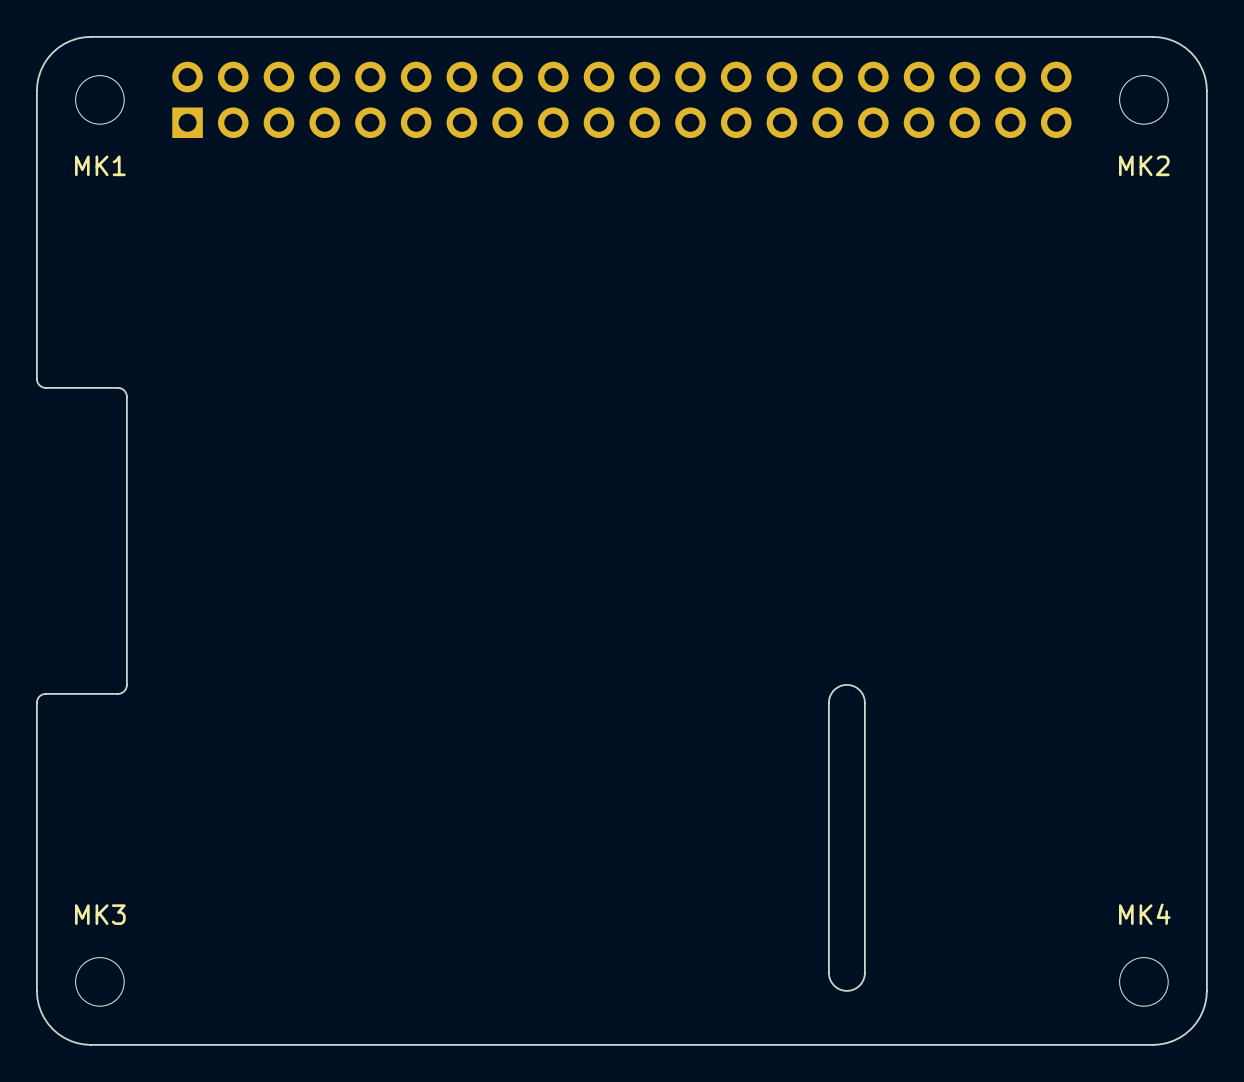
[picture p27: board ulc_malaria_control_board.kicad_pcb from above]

Board: 2 copper layers, 65.0 x 56.0 mm, 5 parts (1 on the bottom side), 3 nets, no tracks yet.

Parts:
MK1, MK2, MK3, MK4: M2.5; MountingHole_2.7mm_M2.5
P1: Conn_02x20_Odd_Even; PinSocket_2x20_P2.54mm_Vertical

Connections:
+3V3: P1.1, P1.17
+5V: P1.2, P1.4
GND: P1.6, P1.9, P1.14, P1.20, P1.25, P1.30, P1.34, P1.39

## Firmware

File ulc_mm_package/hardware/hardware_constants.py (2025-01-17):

from ulc_mm_package.scope_constants import ACQUISITION_FPS


# ================ Misc constants ================ #
RPI_OUTPUT_V = 3.3
BOARD_STATUS_INDICATOR = 4

# ================ EWMA filter constants ================ #
FOCUS_EWMA_ALPHA = 0.05

# ================ Camera constants ================ #
DEFAULT_EXPOSURE_MS = 0.5
DEVICELINK_THROUGHPUT = 200000000

CAMERA_FPS = 53

# ================ Motor controller constants ================ #
FULL_STEP_TO_TRAVEL_DIST_UM = 0.56
DEFAULT_FULL_STEP_HOMING_TIMEOUT = 15

# Pin numbers in BCM, see https://pinout.xyz/
MOTOR_ENABLE = 6
MOTOR_SLEEP = 26
MOTOR_RESET = 21
MOTOR_STEP_PIN = 19
MOTOR_DIR_PIN = 16
MOTOR_FAULT_PIN = 20
MOTOR_LIMIT_SWITCH1 = 18
ZERO_OFFSET_STEPS = 20

# DRR8825 stepping mode reference
RESOLUTION = {
    "Full": (0, 0, 0),
    "Half": (1, 0, 0),
    "1/4": (0, 1, 0),
    "1/8": (1, 1, 0),
    "1/16": (0, 0, 1),
    "1/32": (1, 0, 1),
}

# ================ Encoder constants ================ #
ROT_INTERRUPT_PIN = 27
ROT_A_PIN = 12
ROT_B_PIN = 3
ROT_C_PIN = 11

# ================ LED Driver constants ================ #
LED_PWM_PIN = 13
LID_LIMIT_SWITCH2 = 15

# To activate analog dimming mode, the voltage must be between the following bounds. For analog
# dimming mode, the voltage must be higher than the upper bound listed below.
PWM_DIM_MODE_LOWER_THRESHOLD_V = 1
PWM_DIM_MODE_UPPER_THRESHOLD_V = 2.07
PWM_DIM_MODE_DUTYCYCLE = (
    (PWM_DIM_MODE_LOWER_THRESHOLD_V + PWM_DIM_MODE_UPPER_THRESHOLD_V) / 2
) / RPI_OUTPUT_V
ANALOG_DIM_MODE_DUTYCYCLE = 1

# To ensure linear dimming performance, PWM must be <1kHz (see datasheet pg. 19)
LED_FREQ = 50000

# ================ Pressure control constants ================ #
SERVO_5V_PIN = 17
SERVO_PWM_PIN = 12
VALVE_PIN = 8
SERVO_FREQ = 100
DEFAULT_SYRINGE_MAX_DUTY_CYCLE = 0.23
DEFAULT_SYRINGE_MIN_DUTY_CYCLE = 0.16
DEFAULT_STEP = (DEFAULT_SYRINGE_MAX_DUTY_CYCLE - DEFAULT_SYRINGE_MIN_DUTY_CYCLE) / 60

PRESSURE_SENSOR_ENABLE_PIN = 22
STALE_PRESSURE_VAL_TIME_S = 3
DEFAULT_AFC_DELAY_S = 1
AFC_NUM_IMAGE_PAIRS = 12

MPRLS_RST = 10
MPRLS_PWR = 22

MIN_PRESSURE_DIFF = 330  # In units of hPa
# ================ Fan constants ================ #
FAN_GPIO = 5
CAM_FAN_1 = 23
CAM_FAN_2 = 24

# ================ RTC constants ================ #
DATETIME_FORMAT = "%Y-%m-%d-%H%M%S"

# ================ TH sensor update period ================ #
# TH sensor update period
TH_PERIOD_S = 5
TH_PERIOD_NUM = int(TH_PERIOD_S * ACQUISITION_FPS)

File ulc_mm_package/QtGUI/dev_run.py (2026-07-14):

from datetime import datetime, timedelta
import os
from os import listdir
from pathlib import Path
import re
import socket
import sys
import traceback
import subprocess
from typing import Dict
from time import perf_counter, sleep

import cv2
import numpy as np
from PyQt5 import QtWidgets, uic  # type: ignore
from PyQt5.QtCore import Qt, QThread, pyqtSignal, pyqtSlot
from PyQt5.QtGui import QImage, QPixmap
from qimage2ndarray import gray2qimage
from gpiozero import CPUTemperature

from ulc_mm_package.hardware.hardware_constants import DATETIME_FORMAT
from ulc_mm_package.hardware.real.camera import BinningMode
from ulc_mm_package.scope_constants import (
    SSD_DIR,
    VIDEO_PATH,
    VIDEO_REC,
    SIMULATION,
)
from ulc_mm_package.hardware.scope import MalariaScope, Components
from ulc_mm_package.hardware.motorcontroller import (
    Direction,
    MotorControllerError,
    MotorInMotion,
)
from ulc_mm_package.hardware.led_driver_tps54201ddct import LEDError
from ulc_mm_package.hardware.pim522_rotary_encoder import EncoderI2CError
from ulc_mm_package.hardware.pneumatic_module import (
    PneumaticModule,
    PneumaticModuleError,
    PressureSensorNotInstantiated,
    SyringeInMotion,
    SyringeEndOfTravel,
    PressureSensorStaleValue,
)
from ulc_mm_package.hardware.scope_routines import Routines
from ulc_mm_package.image_processing.autobrightness import (
    BrightnessTargetNotAchieved,
    BrightnessCriticallyLow,
    LEDNoPower,
)
from ulc_mm_package.image_processing.flow_control import (
    FlowController,
    CantReachTargetFlowrate,
)
from ulc_mm_package.image_processing.zstack import (
    full_sweep_image_collection,
    local_sweep_image_collection,
)

from ulc_mm_package.neural_nets.neural_network_constants import IMG_RESIZED_DIMS

from ulc_mm_package.image_processing.processing_constants import FLOWRATE

from ulc_mm_package.neural_nets.AutofocusInference import AutoFocus
import ulc_mm_package.neural_nets.neural_network_constants as nn_constants

cpu = CPUTemperature()

QtWidgets.QApplication.setAttribute(Qt.AA_EnableHighDpiScaling, True)

# Qt GUI Files
curr_dir = Path(__file__).parent.resolve()  # Get full path
os.chdir(curr_dir)
_UI_FILE_DIR = curr_dir / "dev_run.ui"


class ApplicationError(Exception):
    """Catch-all exception for misc errors not caught by the peripheral classes."""

    pass


class AcquisitionThread(QThread):
    # Qt signals must be defined at the class-level (not instance-level)
    changePixmap = pyqtSignal(QImage)
    motorPosChanged = pyqtSignal(int)
    zStackFinished = pyqtSignal(int)
    updatePressure = pyqtSignal(float)
    measurementTime = pyqtSignal(int)
    fps = pyqtSignal(int)
    temperatures = pyqtSignal(int)
    pressureLeakDetected = pyqtSignal(int)
    syringePosChanged = pyqtSignal(int)
    flowValChanged = pyqtSignal(float)
    autobrightnessDone = pyqtSignal(int)
    doneSaving = pyqtSignal(int)

    def __init__(self, external_dir, mscope: MalariaScope):
        super().__init__()
        self.mscope = mscope
        self._initializeAttributes(external_dir, mscope)
        if mscope.getComponentStatus()[Components.CAMERA]:
            self.camera = mscope.camera
            self.camera_activated = True
        else:
            self.camera_activated = False

    def _initializeAttributes(self, external_dir: str, mscope: MalariaScope):
        """Initialize attributes (variables, flags, references to hardware peripherals)
        in this function to make the __init__ more readable."""

        # Flags and counters
        self.im_counter = 0
        self.update_liveview = 1
        self.update_counter = 0
        self.num_loops = 50
        self.camera_activated = False
        self.main_dir = None
        self.single_save = False
        self.continuous_save = False
        self.liveview = True
        self.takeZStack = False
        self.custom_image_prefix = ""
        self.updateMotorPos = True
        self.updateSyringePos = True
        self.fps_timer = perf_counter()
        self.start_time = perf_counter()
        self.external_dir = external_dir
        self.click_to_advance = False
        self.finish_saving_future = None

        # Hardware peripherals
        self.motor = mscope.motor
        self.pneumatic_module: PneumaticModule = mscope.pneumatic_module
        mscope._init_data_storage(fps_lim=40)
        self.data_storage = mscope.data_storage

        # Routines
        self.routines = Routines()
        mscope.flow_controller.reset()
        self.flow_controller: FlowController = mscope.flow_controller
        self.initializeFlowControl = False
        self.flowcontrol_enabled = False
        self.fast_flow_enabled = False
        self.autobrightness = self.routines.autobrightnessRoutine(mscope)
        self.autobrightness_on = False
        self.timestamp = 0

        # Single-shot autofocus
        try:
            self.autofocus_model = AutoFocus()
        except RuntimeError as e:
            raise RuntimeError(
                f'got {str(e)}:\n {subprocess.getoutput("lsusb | grep Myriad")}'
            )
        self.active_autofocus = False
        self.prev_autofocus_time = 0.0
        self.af_adjustment_done = False

    def run(self):
        while True:
            if self.camera_activated:
                try:
                    for image, timestamp in self.camera.yieldImages():
                        self.timestamp = timestamp
                        self.updateGUIElements()
                        self.save(image)
                        self.zStack(image)
                        self.activeFlowControl(image)
                        self._autobrightness(image)
                        self.autofocusWrapper(image)

                        if self.liveview:
                            if self.update_counter % self.update_liveview == 0:
                                qimage = gray2qimage(image)
                                self.changePixmap.emit(qimage)
                        elif self.click_to_advance:
                            qimage = gray2qimage(image)
                            self.changePixmap.emit(qimage)
                            self.click_to_advance = False
                except Exception as e:
                    # This catch-all is here temporarily until the PyCameras error-handling PR is merged (https://github.com/czbiohub/pyCameras/pull/5)
                    # Once that happens, this can be swapped to catch the PyCameraException
                    print(e)
                    print(traceback.format_exc())

    def getMetadata(self) -> Dict:
        """Required metadata:
        - Measurement type (actual diagnostic experiment or data collection)
        - Sample type / sample name (i.e dataset name)
        - Timestamp
        - Motor position
        - Syringe position
        - Pressure reading
        - Ambient temperature (updated every N Frames)
        - RPi CPU temperature (updated every N frames)
        - Focus metric (updated every N frames)
        - LED power
        """

        try:
            pressure, pressure_sensor_status = self.pneumatic_module.getPressure()
        except PressureSensorNotInstantiated:
            # TODO: Add logging
            pressure = -1
            pressure_sensor_status = -1
        except PressureSensorStaleValue as e:
            # TODO: Add logging
            print(f"Stale value from pressure sensor: {e}")
            pressure = -1
            pressure_sensor_status = -1

        return {
            "im_counter": self.im_counter,
            "measurement_type": "placeholder",
            "sample_type": "placeholder",
            "timestamp": self.timestamp,
            "exposure": self.camera.exposureTime_ms,
            "motor_pos": self.motor.pos,
            "pressure_hpa": pressure,
            "pressure_status_flag": pressure_sensor_status.value,
            "syringe_pos": self.pneumatic_module.getCurrentDutyCycle(),
            "flow_control_on": self.flowcontrol_enabled,
            "target_flowrate": self.flow_controller.target_flowrate,
            "current_flowrate": self.flow_controller.flowrate,
            "focus_adjustment": self.af_adjustment_done,
        }

    def save(self, image):
        if self.single_save:
            self.data_storage.writeSingleImage(image, self.custom_image_prefix)
            self.single_save = False

        if self.continuous_save:
            if self.data_storage.is_writable():
                self.data_storage.writeData(image, self.getMetadata(), self.im_counter)
                self.measurementTime.emit(int(perf_counter() - self.start_time))
                self.im_counter += 1

    def updateGUIElements(self):
        self.update_counter += 1
        if self.updateMotorPos:
            self.motorPosChanged.emit(self.motor.pos)

        if self.updateSyringePos:
            self.syringePosChanged.emit(1)

        if self.update_counter % self.num_loops == 0:
            self.update_counter = 0
            if self.pneumatic_module is not None:
                try:
                    # TODO: do something with the status
                    (
                        pressure,
                        pressure_sensor_status,
                    ) = self.pneumatic_module.getPressure()
                    self.updatePressure.emit(pressure)
                except Exception:
                    pressure = -1
                    self.updatePressure.emit(pressure)
            self.fps.emit(int(self.num_loops / (perf_counter() - self.fps_timer)))
            self.fps_timer = perf_counter()

            # Update temperatures
            self.temperatures.emit(1)

        if self.finish_saving_future is not None:
            if self.finish_saving_future.done():
                self.doneSaving.emit(1)
                self.finish_saving_future = None

    def updateExposure(self, exposure):
        self.camera.exposureTime_ms = exposure

    def takeImage(self):
        if self.main_dir is None:
            self.data_storage.createTopLevelFolder(
                self.external_dir, datetime.now().strftime(DATETIME_FORMAT)
            )
            self.main_dir = self.data_storage.main_dir

        if self.continuous_save:
            hostname = re.sub(r"[^A-Za-z0-9._-]", "-", socket.gethostname())
            exp_name = f"{self.custom_image_prefix}-{hostname}"
            self.data_storage.createNewExperiment(
                self.external_dir,
                custom_experiment_name=exp_name,
                datetime_str=datetime.now().strftime(DATETIME_FORMAT),
                experiment_initialization_metadata={},
                per_image_metadata_keys=self.getMetadata().keys(),
            )

            self.im_counter = 0
            self.start_time = perf_counter()

    def changeBinningMode(self):
        if self.camera_activated:
            self.camera.stopAcquisition()
            self.camera_activated = False

        if self.camera.getBinning() == 2:
            print("Changing to 1x1 binning.")
            self.binning = 1
            self.camera.setBinning(bin_factor=1, mode=BinningMode.AVERAGE)
        else:
            print("Changing to 2x2 binning.")
            self.binning = 2
            self.camera.setBinning(bin_factor=2, mode=BinningMode.AVERAGE)

        self.camera_activated = True

    def runFullZStack(self):
        self.takeZStack = True
        self.zstack = full_sweep_image_collection(
            motor=self.motor,
            steps_per_coarse=10,
            save_loc=self.external_dir,
            custom_name=self.custom_image_prefix,
        )
        self.zstack.send(None)

    def runLocalZStack(self):
        self.takeZStack = True
        self.mscope.fan.turn_off_all()
        self.zstack = local_sweep_image_collection(
            self.motor,
            self.motor.pos,
            save_loc=self.external_dir,
            custom_name=self.custom_image_prefix,
        )
        self.zstack.send(None)
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

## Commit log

2023-03-07 printout exception
2023-03-21 add component status check for the pressure sensor (#376)
2023-05-01 Update pneumatic_utility.py
    Add print
2023-05-04 flowrate refactor (#392)
2023-05-24 Flow control error refactor
2023-05-24 Check if current state is pause-able
2023-05-31 Turn on power to servo and create 'None' enum for camera
2023-05-31 remove camera selection from `neural_nets` as it is no longer needed
2023-05-31 fix error reporting for unknown enum in CameraOptions dimension method
2023-05-31 update camera selection message in hardware/scope.py
2023-05-31 fix typing in flowrate
2023-05-31 Update pneumatic_utility.py
    add axis labels to calibration plot
2023-05-31 Switch motorcontroller steptype from string to enum (#406)
2023-05-31 Update pneumatic_utility.py
    Let it run the servo when the pressure sensor is bricked.
2023-06-01 camera error instead of runtime error
2023-06-03 Address PR comments
    - Add return type None to calibrate_range
    - Add error handling to set_pwm method
    - Narrow scope of try/finally in main()
    - Use list comprehension for _viable_videos
    - Remove raised exceptions from scope_constants.py because it's too specific and prevents standalone test scripts from running
2023-06-05 else case to satiate mypy
2023-06-13 Add print out of final cell count and average confidence per class
2023-06-13 Removed print statements
2023-06-18 bugfix - typo + add filtering for specific type of cell and filtering for values above/below confidence threshold
2023-06-20 actually connect signal/slot this time
2023-06-20 bugfix for case where nothing is predicted for the very first frame
2023-06-22 keep current pred tensor in state
2023-06-28 add nms filtering to predictions_handler
2023-06-30 catch temp/humiidty sensor exception on dev_run
2023-07-11 Run SSAF on every frame
2023-07-13 upper case
2023-07-18 tpu after flowcontrol
2023-08-09 turn camera off while closing experiment, turn it back on after
2023-08-09 print statement for creating report
2023-08-11 ThreadPoolExecutor for saving subsample / parasite thumbnails (#449)
2023-08-14 use log scale if array is nonzero (otherwise this prints a warning in the terminal)
2023-08-14 sneak in removing a cheeky print statement
2023-08-14 When flowrate errors out, flow control effectively stops however currently we still send images and reinstantiate the routine. This wastes some computation but more critically clutters up the termina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
2023-08-14 reset flow control error raised flag when entering pause state (since we redo all the setup stages at that point)
2023-08-15 change flowrate label when flow control fails
2023-09-08 add confidence filtering for getting cell counts
2023-09-08 add led pwm value to the per image metadata
2023-09-16 add camera temperature to per-img metadata
2023-09-16 only log camera temperature when we get a new reading
2023-09-19 Revert "Camera temp log"
2023-10-04 add more graceful shutdowns of work in NCS classes
    ThreadPoolExecutor.shutdown(wait=True) will start executing every function in
    it's queue, but will cancel each object immediately. Boo!
    This more gracefully waits for the work queue to finish, and then for the NCS's
    queues to finish
2023-10-25 defensively restart the autofocus model and the cell diagnosis model
    IJ found a bug where the start of the predictions handler would have some references to very high image numbers.
    Perhaps this is due to the NCSModel thread pool executors not being reset between runs?
    This PR defensively resets them, and also shuts them down at the end of an experiment (but that should be unecessary,
    since the GC will take care of it anyways)
2023-11-01 Turned stats utils into a class
    [confusion_matrix.csv]
2023-11-09 add heatmaps to PredictionHandler
2023-11-09 Save the raw heatmaps at the end of the run
2023-11-09 misplaced bracket
2023-12-05 Minor printout format change
2023-12-19 Change printout
2024-01-18 Edit final printout
2024-01-18 Add formatting to stats print
2024-01-19 Remove extra print statements
2024-02-09 Remove duplicate code for downsample_img. Bubble up downsampling up from flowrate and into `scope_op`. This is being done because the classic image focus metric will also require a downsampled image,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
2024-02-09 Reset ClassicFocus after cellfinder, autofocus1, and autofocus2 to minimize the chance that its EWMA filter is initialized with a poor value
2024-02-13 Init flowrate multiproc with downscaled dims
2024-02-13 set ht/wt based on camera selection
2024-02-13 Init flow controller with controller with downsampled dimensions
2024-02-14 flowrate bugfix
2024-02-14 add motor not moving check to end_cellfinder
2024-02-14 fast flow error dialog only on initial setup
2024-02-15 thread pool executor shutdown is quite neat!
2024-02-15 Remove low confidence xcorr exception; it was not being used and mroe importantly, had the potential to cause a very serious issue. During a cellfinder step triggered after an OOF exception, the syri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
2024-02-16 area filter
2024-02-17 Replace stats utils with stats_utils repo
    [confusion_matrix.csv]
2024-02-20 Add sample dropdown menu to experiment form
2024-02-20 Add check for clinical vs. cultured based on sample type list
2024-02-21 area filtering in _parse_prediction_tensor
2024-03-27 Add more cohesive sample list, including option to skip compensation
2024-03-27 Accomodate other sample types in CountCompensator initialization
2024-03-29 Update the flow control routine so that the generator doesn't fail (StopIteration exception) when the syringe reaches its maximum position. Instead, return a boolean indicating whether the syringe is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
    This commit changes the behaviour of the flow control routine so that it yields the syringe move boolean. This allows the routine to continue to accept images
    and measure flowrate, even if the syringe cannot move. Previously, when the exception was raised, the generator dies. Reinitializing the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
2024-03-29 add nonnull check for syringe_can_move var
2024-03-30 When returning from an OOF exception and doing cell finder, skip pulling the syringe
2024-04-03 bubble up the logging statement and add logic so it only emits once when the syringe hits its end of travel
2024-04-16 increase area thresh filter
2024-04-23 Add flowchart
2024-06-02 Retain polished-dragon model files in a folder - can explicitly switch to that model for old flow cells when needed by changing AUTOFOCUS_MODEL_NAME in neural_network_constants.py (e.g for Ohmu @ Der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
2024-07-22 Added autobrightness post flow
2024-08-07 Remove extra square bracket
2024-08-08 Fix area filtering bug - previously we were erroneously using an area filter value that was normalized to the image dimensions. That is what we would need to use if we were processing the raw YOGO ou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
2024-08-08 Run autobrightness routine continuously during an acquisition, constant in image_processing/processing_constants.py set to running it once every 30 frames for now
2024-08-08 img id shape should be created after area filtering is done
2024-09-23 Set flowrate to medium (no user selection)
2024-09-23 Replace old TARGET_FLOWRATE with medium flowrate
2024-09-23 revert to prints since the logger has not been instantiated yet
2024-09-23 Include flowrate options
2024-09-24 Use full enum for target flowrate
2024-09-24 Format flowrate name and val in metadata
2024-09-24 Capitalize flowrate name
2024-09-25 Initial working heatmap
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2024-10-04 Fix model dir in exp metadata and log stel pressure exception
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2024-12-19 fix cannot reach target flowrate bug
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2025-01-06 In CellFinder, account for the case where the max allowable pressure cannot be reached. For now, continue with the rest of the routine. If there is indeed a serious pressure issue, then cells will no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
2025-01-31 Add monitoring and dialog box exception if a pressure leak is detected during a run.
2025-02-28 Setting NCS performance hit will potentially allow for more frequent polling of SSAF, and thus improve our ability to track focal drift. May want to tweak EWMA parameters to be less conservative sinc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
2025-03-07 This was the main problem - we should not instantiate a new FlowController instance, use mscope's existing one
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2025-03-10 Revert "Merge branch 'develop' into pressure_leak_warning"
    This reverts commit 18022466e8a8636d5b11bf58606d9e2e1a57d4c1, reversing
    changes made to 60da54804418886fb0150d4b13503edaedfd41f3.
2025-03-12 Context: We set the pneumatic module step size to be twice what it is normally when doing fast flow, so that the set up is quicker and more ergonomic for the user (i.e they don't need to wait for a l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
2025-03-14 Replaced print statements with logger. Added additional debug logging. Added new log file on new experiment
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2025-06-06 Update setup.sh to improve log parsing
    The filename label was dropped due to its high cardinality which would slow down Loki. However, this causes all log files to enter into one stream. Multiple buffers are parsing log files at once. Whe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
